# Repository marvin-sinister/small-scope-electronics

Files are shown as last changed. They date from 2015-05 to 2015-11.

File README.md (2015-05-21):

# small-scope-electronics
Schematics for [small-scope](https://github.com/marvin-sinister/small-scope) arduino oscilloscope



This is a kicad project containing schematics and PCB for [small-scope](https://github.com/marvin-sinister/small-scope) arduino shield.

The shield has not yet been tested, so treat with care. The PCB is single sided so should be reasonably simple to make.

Some of the features:
 * 1, 5, 10, 20 attenuation
 * digital or analog trigger threshold
 * optional external Vref
 * AC/DC choice
 * some safety™
 * power supply choice

*some safety™* being the resistor/zenner circuit at OP amp to µc, which should help keep the ATmega safe within reason.

*power supply choice* means that the OP amp can be powered with either 5V from USB or whatever you connect to Vin (so up to 12V, 9V recommended).

The reason for this is the fact that the LM324N will output voltages in ~0.6-3.8V range on 5V supply. The 9V should have plenty of room to reach the 5V. It would be ideal to have some negative voltage and OP amp which can be biased to increase the range to 0-5V, but that would complicate the whole thing beyond the idea of being simple.

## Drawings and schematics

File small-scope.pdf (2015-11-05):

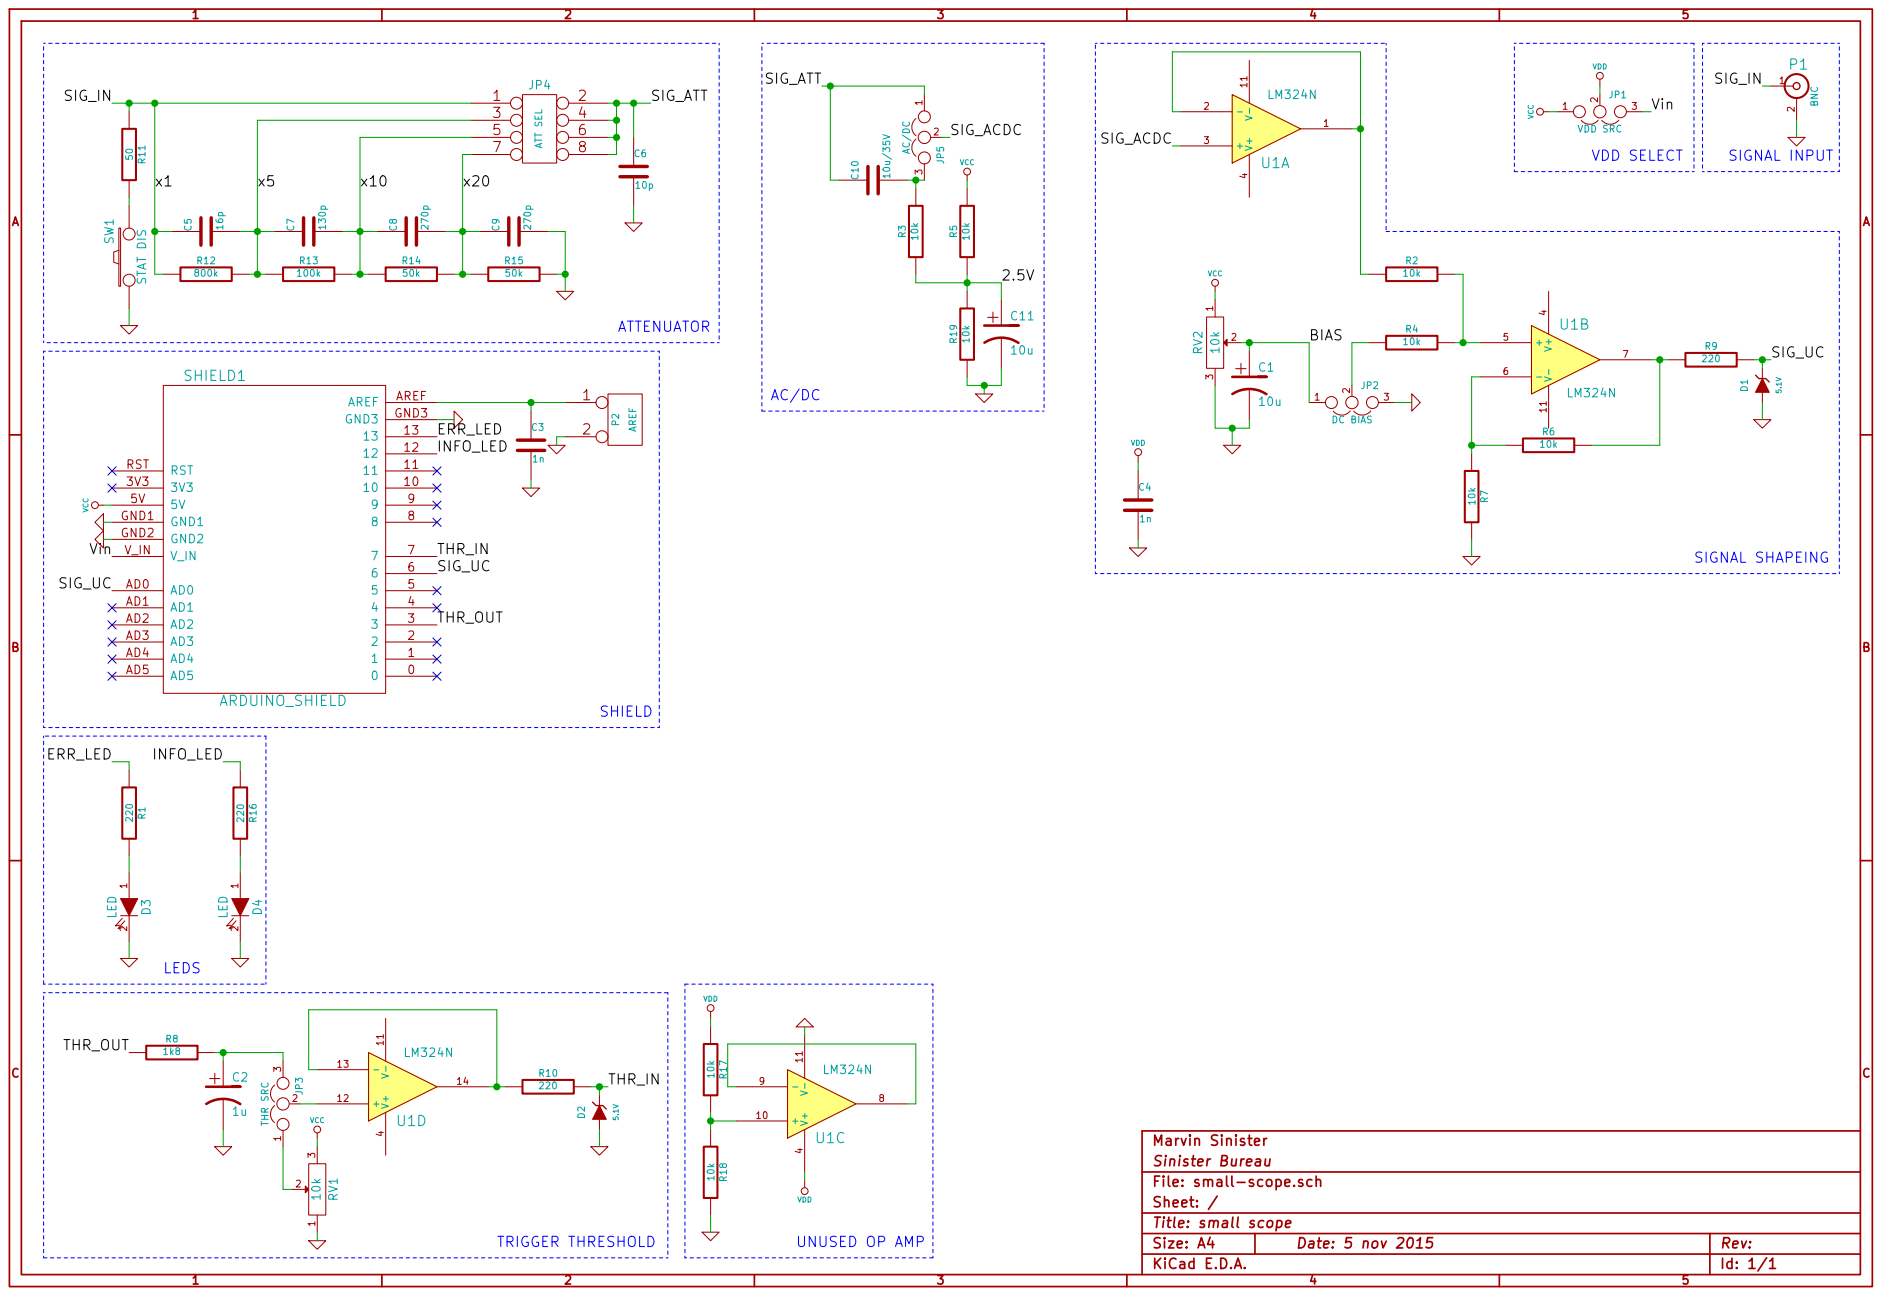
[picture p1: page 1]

Sinister Bureau
File: small-scope.sch
Sheet: /
Title: small scope

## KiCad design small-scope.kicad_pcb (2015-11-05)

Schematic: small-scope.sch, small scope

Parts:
C1, C11: 10u
C2: 1u
C3, C4: 1n
C5: 16p
C6: 10p
C7: 130p
C8, C9: 270p
C10: 10u/35V
D1, D2: 5.1V
D3, D4: LED
JP1: VDD SRC
JP2: DC BIAS
JP3: THR SRC
JP4: ATT SEL
JP5: AC/DC
P1: BNC
P2: AREF
R1, R9, R10, R16: 220
R2, R3, R4, R5, R6, R7, R17, R18, R19: 10k
R8: 1k8
R11: 50
R12: 800k
R13: 100k
R14, R15: 50k
RV1, RV2: 10k
SHIELD1: ARDUINO_SHIELD
SW1: STAT DIS
U1: LM324N

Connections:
/2.5V: C11.1, R3.1, R5.1, R19.2
/BIAS: C1.1, JP2.1, RV2.2
/ERR_LED: R1.1, SHIELD1.13
/INFO_LED: R16.2, SHIELD1.12
/SIG_ACDC: JP5.2, U1.3 (+)
/SIG_ATT: C6.1, C10.1, JP4.2, JP4.4, JP4.6, JP4.8, JP5.1
/SIG_IN: C5.1, JP4.1, P1.1 (In), R11.1, R12.1
/SIG_UC: D1.2, R9.2, SHIELD1.6, SHIELD1.AD0
/THR_IN: D2.2, R10.2, SHIELD1.7
/THR_OUT: R8.1, SHIELD1.3
/Vin: JP1.3, SHIELD1.V_IN
/x5: C5.2, C7.1, JP4.3, R12.2, R13.1
/x10: C7.2, C8.1, JP4.5, R13.2, R14.1
/x20: C8.2, C9.1, JP4.7, R14.2, R15.1
GND: C1.2, C2.2, C3.2, C4.2, C6.2, C9.2, C11.2, D1.1, D2.1, D3.2 (K), D4.2 (K), JP2.3, P1.2 (Ext), P2.2 (PM), R7.2, R15.2, R18.2, R19.1, RV1.1, RV2.3, SHIELD1.GND1, SHIELD1.GND2, SHIELD1.GND3, SW1.1, U1.11 (V-)
unnamed: R11.2, SW1.2
unnamed: JP3.2, U1.12 (+)
unnamed: JP3.1, RV1.2
unnamed: R2.1, U1.1, U1.2 (-)
unnamed: R2.2, R4.2, U1.5 (+)
unnamed: R6.1, R7.1, U1.6 (-)
unnamed: R6.2, R9.1, U1.7
unnamed: R10.1, U1.13 (-), U1.14
unnamed: JP2.2, R4.1
unnamed: C3.1, P2.1, SHIELD1.AREF
unnamed: C10.2, JP5.3, R3.2
unnamed: R17.2, R18.1, U1.10 (+)
unnamed: D3.1 (A), R1.2
unnamed: U1.8, U1.9 (-)
unnamed: D4.1 (A), R16.1
unnamed: C2.1, JP3.3, R8.2
VCC: JP1.1, R5.2, RV1.3, RV2.1, SHIELD1.5V
VDD: C4.1, JP1.2, R17.1, U1.4 (V+)

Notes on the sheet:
ATTENUATOR
TRIGGER THRESHOLD
SIGNAL SHAPEING
UNUSED OP AMP
SHIELD
VDD SELECT
SIGNAL INPUT
LEDS
AC/DC

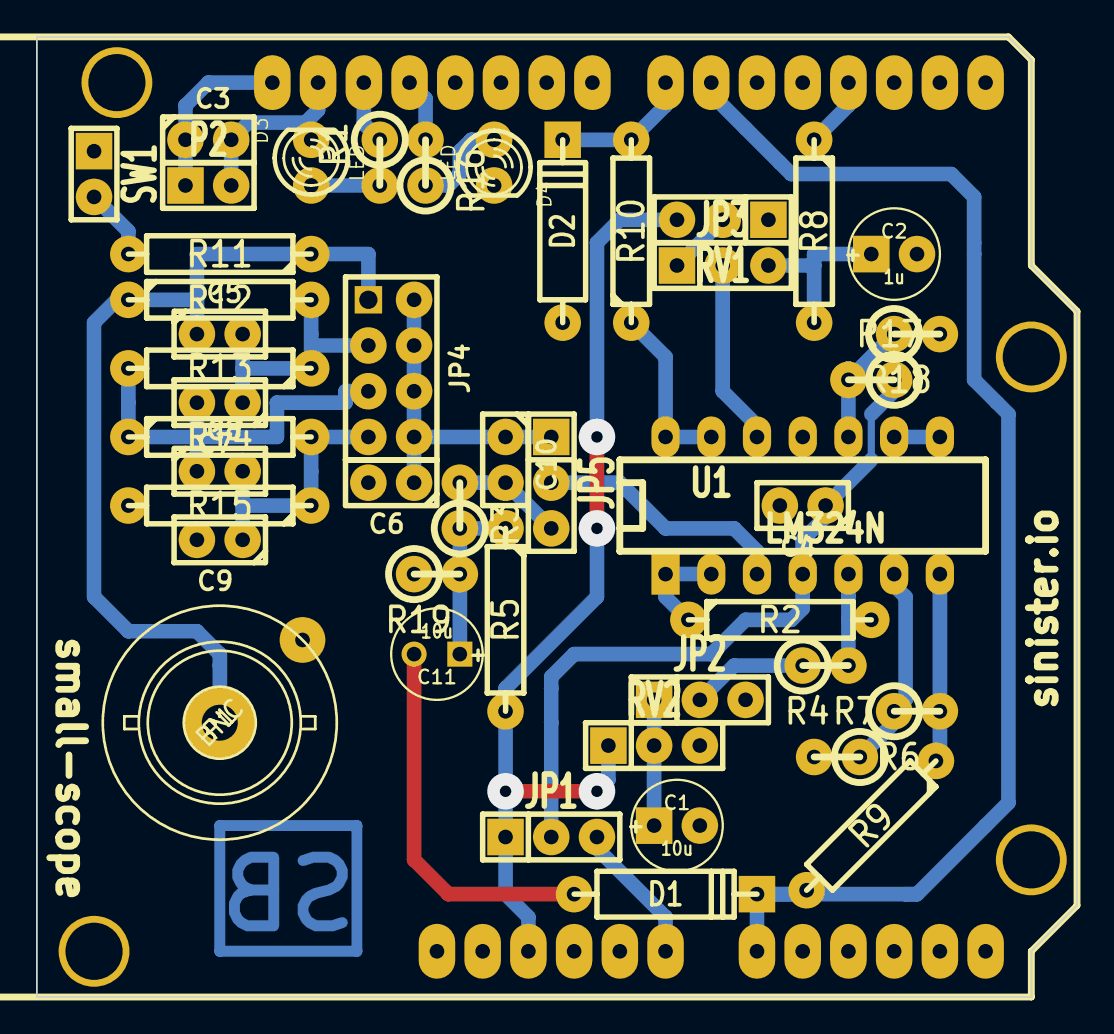
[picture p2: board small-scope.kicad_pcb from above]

Board: 2 copper layers, 57.8 x 53.3 mm, 46 parts (0 on the bottom side), 33 nets.

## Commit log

2015-05-21 initial placement
    [small-scope.kicad_pcb, small-scope.sch]
2015-05-21 general PCB connections
    [small-scope.kicad_pcb]
2015-05-21 routing done
    [small-scope.kicad_pcb, small-scope.sch]
2015-07-11 added AC/DC select and separate DC bias
    [small-scope.kicad_pcb, small-scope.sch]
2015-07-13 board rev1
    [small-scope.kicad_pcb, small-scope.sch]
2015-11-05 Fixed reversed power supply on OP amp
    [small-scope.kicad_pcb, small-scope.sch]
2015-11-05 changed C11 footprint
    [small-scope.kicad_pcb]
